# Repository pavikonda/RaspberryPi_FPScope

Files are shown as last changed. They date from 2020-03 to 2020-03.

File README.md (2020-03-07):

# RaspberryPi_FPScope
Fourier ptychographic microscope based on a Raspberry Pi. 

Published as:
Aidukas, T., Eckert, R., Harvey, A.R. et al. Low-cost, sub-micron resolution, wide-field computational microscopy using opensource hardware. Sci Rep 9, 7457 (2019). https://doi.org/10.1038/s41598-019-43845-9

This repository contains an instruction set to build the microscope, CAD files, data acqusition and data processing codes.

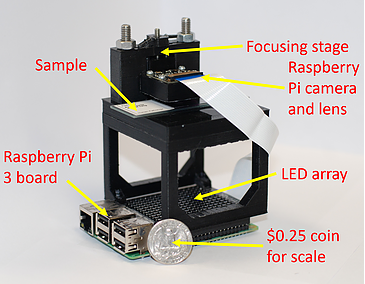
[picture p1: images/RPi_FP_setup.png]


DATA_CAPTURE.py:
This file contains a Python script required to obtain images for Fourier ptychography using a Raspberry Pi computer, Raspberry Pi camera and Unicorn HD LED array. These images are obtained by flashing LEDs in a spiral pattern from the center towards the edges.

CAD Files:
This folder contains .scad and .stl formats of all the parts required to 3D print the microscope. Instructions are outlined in the Supplementary material S1 of our paper.

Fourier ptychographic reconstruction code and test data to use with the reconstruction code can be found at: http://dx.doi.org/10.5525/gla.researchdata.594

Download a Raspbian OS SD card image which includes the necessary libraries from:
https://drive.google.com/open?id=1Z59lnhNKuGGGVIF1KtoCw2bAcdZESKBo

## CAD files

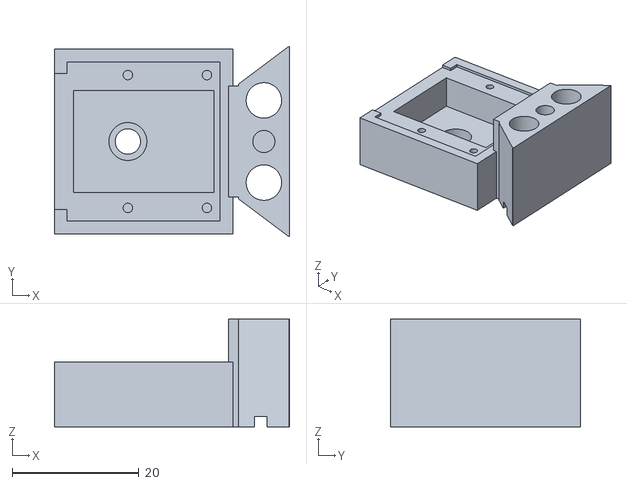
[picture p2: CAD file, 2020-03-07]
CAD files/camera_mount.stl
37.1 x 30.1 x 17.0

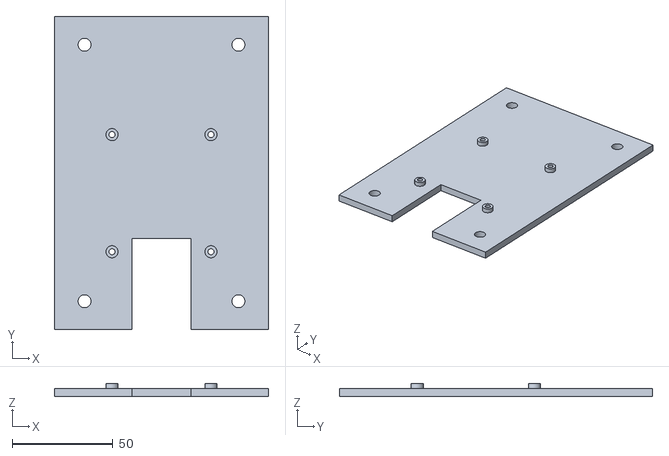
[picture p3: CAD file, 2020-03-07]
CAD files/base.stl
106.0 x 155.0 x 6.50

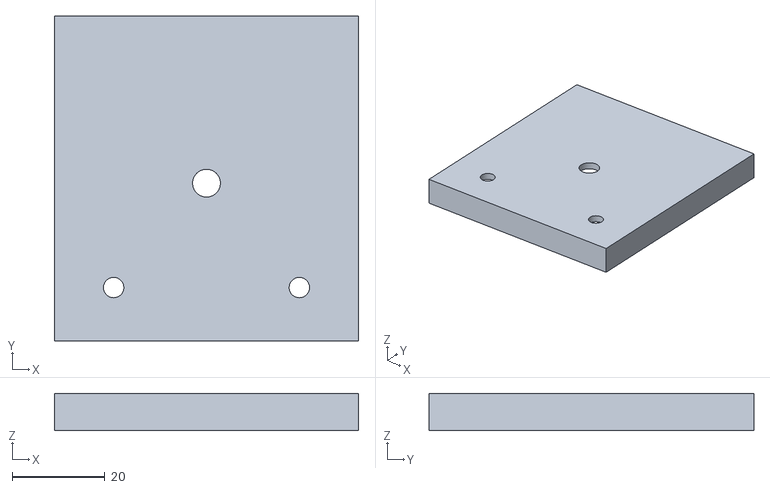
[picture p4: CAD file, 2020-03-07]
CAD files/top.stl
65.5 x 70.0 x 8.00

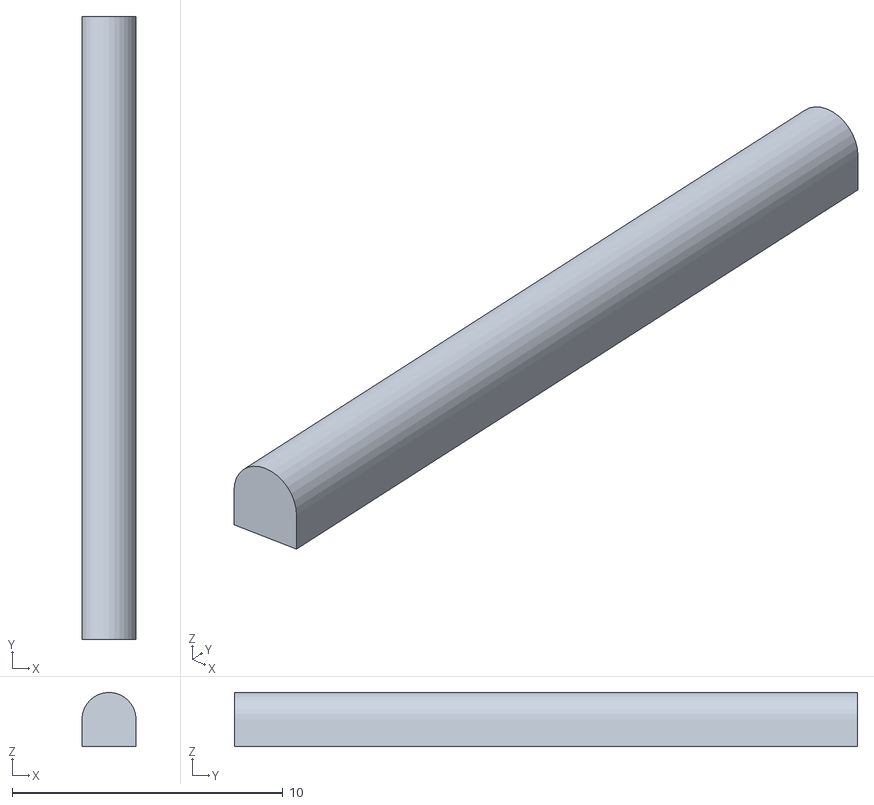
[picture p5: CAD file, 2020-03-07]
CAD files/bar.stl
2.00 x 23.0 x 2.00

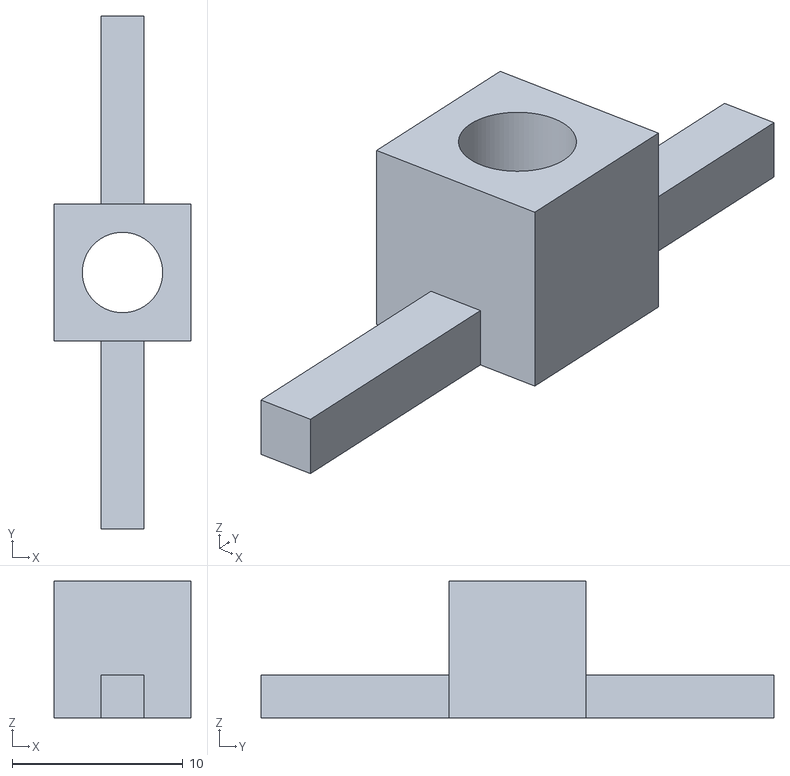
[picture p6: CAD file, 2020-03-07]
CAD files/spring_holder.stl
8.00 x 30.0 x 8.00

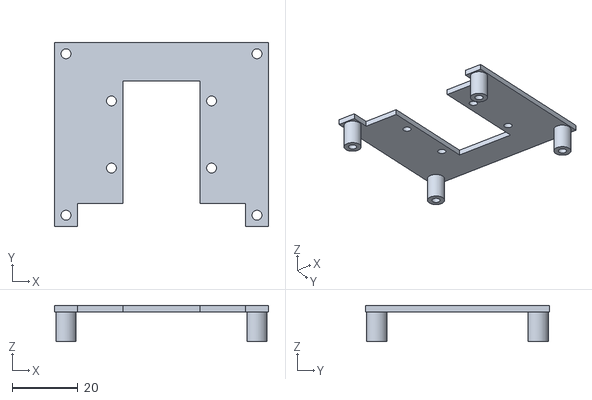
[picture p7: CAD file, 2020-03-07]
CAD files/led_support.stl
65.0 x 56.0 x 11.0

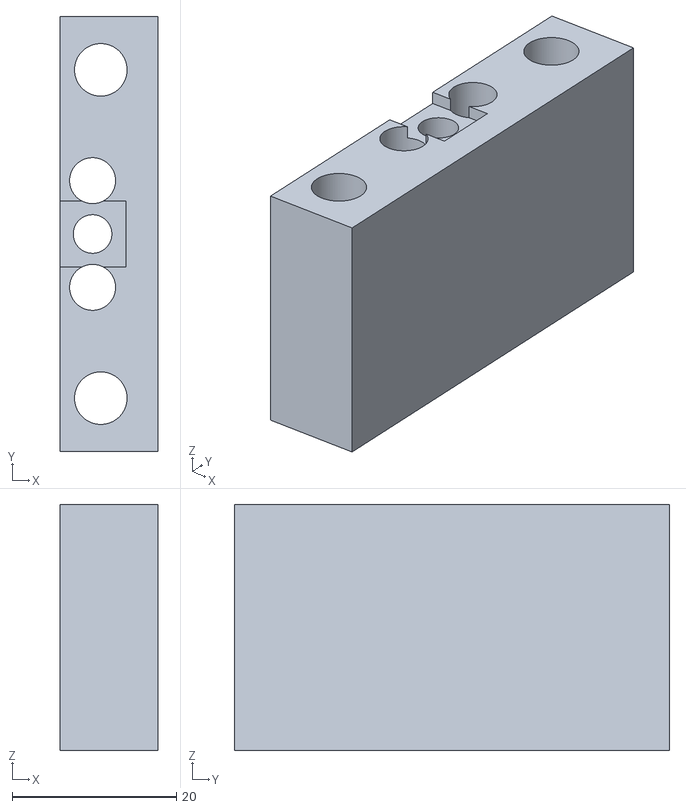
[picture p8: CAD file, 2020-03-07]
CAD files/mount_holder.stl
12.0 x 53.0 x 30.0

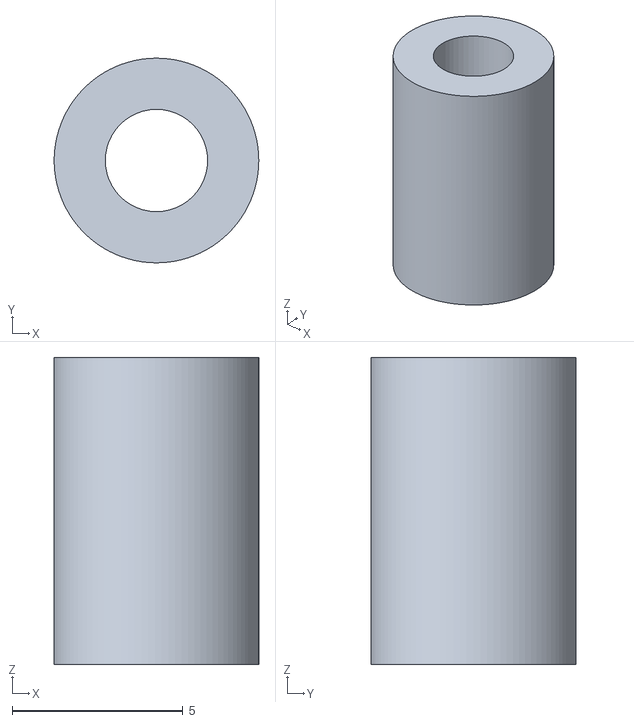
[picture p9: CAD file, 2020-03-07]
CAD files/spacer.stl
6.00 x 6.00 x 9.00

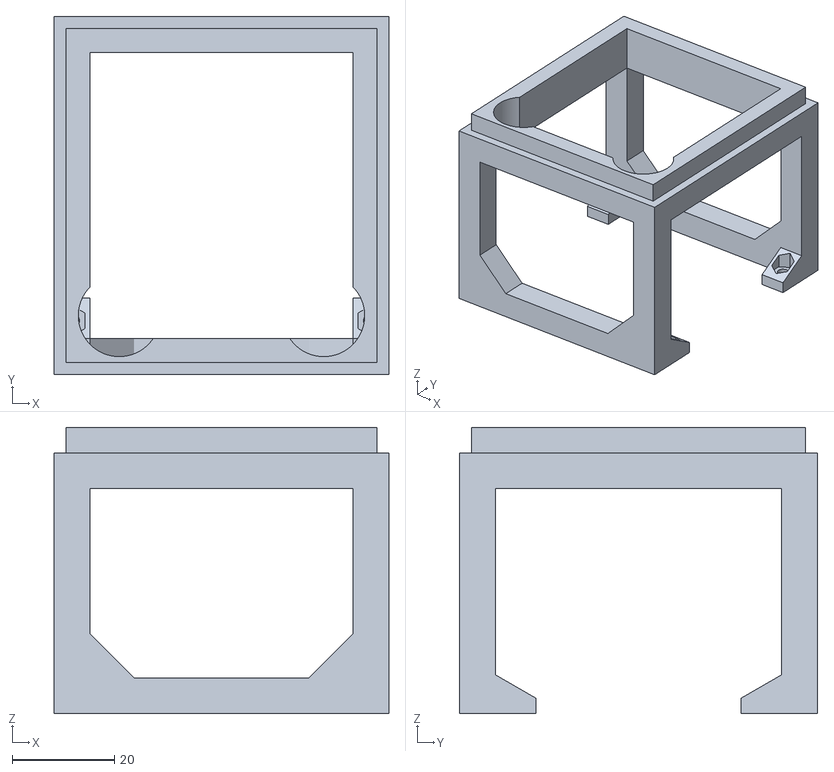
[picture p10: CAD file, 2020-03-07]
CAD files/structure.stl
65.5 x 70.0 x 56.0

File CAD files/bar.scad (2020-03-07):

/*

This is the plastic bar that holds the springs at the bottom of the camera mount (camera_mount.scad)

*/

$fa = 0.2;
$fs = 0.2;

rotate([90,0,0]) cylinder(h=23, r=1,center=true);
translate([0,0,-0.5]) cube([2,23,1], center=true);

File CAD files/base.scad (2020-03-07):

/*

A base for the Raspberry Pi, with attachment holes to mount on an optical table

*/

$fs = 0.2;
$fa = 0.2;

//dimensions of the raspberry pi
pi_width = 56;
pi_length = 85;

//how much the base protrudes from the raspberry pi body
extra_width = 25;
extra_length = 35;

//actual dimensions of the base
total_width = pi_width + extra_width*2;
total_length = pi_length + extra_length*2;
thickness = 4;

//screw dimensions
inner_r = 1.5;
outer_r = 3;
cone_r = 5;

hole_separation_length = 58;
hole_separation_width = 56-3-3-0.5-0.5;

//location of the four holes
hole_x = extra_width + 3 + 0.5;
hole_y = extra_length + 3 + 0.5;
feet_height = 2.5;
hole_height = thickness+feet_height+2;

//location of the four attachment holes
separation = 25.4;
attachment_x = total_width/2 - (separation/2 +separation*1);
attachment_y = total_length/2 - (separation/2 + separation*2);

module foot(){
    cylinder(r=outer_r,h=feet_height);
}
module screw_hole(){
    cylinder(r=inner_r,h=hole_height);
}
module cone_hole(){
    cylinder(r1=cone_r, r2=inner_r,h=thickness);
}
module attachment_hole(){
    cylinder(r=3.2,h=thickness+2);
}

//cutout dimensions
margin = 10;
cutout_x = hole_separation_width-cone_r*2-margin;
cutout_y = extra_length+margin;
module sd_cutout(){
    translate([total_width/2,cutout_y/2-0.01,thickness/2-1]) cube([cutout_x,cutout_y,thickness+3],center=true);
}

module move_raspi_bolts(){
    translate([hole_x,hole_y,0]) children();
    translate([hole_x,hole_y+hole_separation_length,0]) children();
    translate([hole_x+hole_separation_width,hole_y+hole_separation_length,0]) children();
    translate([hole_x+hole_separation_width,hole_y,0]) children();
}

module move_attachment_bolts(){
    translate([attachment_x, attachment_y,-1]) children();
    translate([total_width-attachment_x, attachment_y,-1]) children();
    translate([attachment_x, total_length-attachment_y,-1]) children();
    translate([total_width-attachment_x, total_length-attachment_y,-1]) children();
}

difference(){
    //base with legs
    union(){
        cube([total_width,total_length,thickness]);
        translate([0,0,thickness]) move_raspi_bolts() foot();
    }
    
    //subtract holes from screws
    translate([0,0,-0.001]) move_raspi_bolts(){
        screw_hole(); 
        cone_hole();
    }
    
    //subtract holes for attachment (to the optical table) bolts
    move_attachment_bolts(){
        attachment_hole();
    }
    
    sd_cutout();
}

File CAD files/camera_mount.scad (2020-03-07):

/*

Designed to hold a Raspberry Pi camera module, and fit into mount_holder.scad

Design by Tomas Aidukas, modified by Victor Lovic

*/

// Y is along the cable
camera_w_y = 25.2;
camera_w_x = 24.2;
$fn = 100;
height=14.5-2.8;
wall_thick=4;
lens_height=4;

//Lens is pushed by 1mm from the bottom + its height is 4z.5mm + 6mm distance to the detector lens + the lens sits 6.5mm away from the support. Hence the support should be built 18mm from the bottom
cam_holder = 18;

// Camera platform
difference(){        
        cube([camera_w_x+wall_thick,camera_w_y+wall_thick,height],center=true);
        
    // Crop the top
    translate([0,0,height/2]){
        cube([camera_w_x+1+wall_thick,camera_w_y+1+wall_thick,3],center=true);}
    translate([-10,0,height/2]){
        cube([camera_w_x+10+wall_thick,21.5,4],center=true);}
        
    // Hole inside
    translate([0,0,lens_height]){    
        cube([camera_w_x-2,camera_w_y-9,height+1],center=true);}
    
    // Lens is pushed up by 1mm from the bottomm + its height of 3mm gives 4mm from the bottom of the holder to the top aperture plastic
    translate([-2.5,0,-height/2+lens_height/2+1]){        
        cylinder(d=6, h=lens_height,center=true);}
    
    translate([-2.5,0,-height/2+lens_height/2-1]){        
        cylinder(d=4, h=lens_height,center=true);}
    
    // Camera Holder. The sensor chip sits heigth - 4mm (lens top) - 2mm crop from the top of the lens  = 8mm  . But we also crop 1mm from the bottom of the sensor giving uz 7mm separation from the top lens plastic  to the sensor. Since we need 7.5mm the esensor height = 7.5mm + 2mm + 4mm = 13.5mm
        
    translate([0,0,height/2]){        
        cube([camera_w_x,camera_w_y,4],center=true);}
        
               
    // Camera screw holes
     translate([-24/2+9.5,21/2,height/2-2]){
         cylinder(d=1.5,h=10,center=true);}     
     translate([-24/2+9.5,-21/2,height/2-2]){
         cylinder(d=1.5,h=10,center=true);}
      translate([-24/2+22,21/2,height/2-2]){
         cylinder(d=1.5,h=10,center=true);}
      translate([-24/2+22,-21/2,height/2-2]){
         cylinder(d=1.5,h=10,center=true);}// Camera screw holes END   
         
}



// Slider
// angle is tan(delta_h/slider_hole_w_h)
slider_hole_w_h = 30; 
slider_x_shift_h = 10;
slider_z_shift_h = -10;
delta_h = -20;
$fn = 100;
height1 = height-1.5+2.8+4;
// To get the same angle we need arctan(tan(delta_h/slider_hole_w_h))*slider_hole_w = delta

//30mm is too loose
slider_hole_w = 30; 
slider_x_shift = 10;
slider_z_shift = -10;
//delta = -20;
delta = atan(tan(delta_h/slider_hole_w_h))*slider_hole_w;

camera_w = 25+4;

translate([13,0,height/2+2+2.8+2]){
difference(){
    hull(){
        translate([slider_x_shift,slider_hole_w/2,slider_z_shift]){
            cube([0.1,0.1,height1], center=true);
        }
        
        translate([slider_x_shift,-slider_hole_w/2,slider_z_shift]){
            cube([0.1,0.1,height1], center=true);
        }
        
        translate([slider_x_shift+delta,0,slider_z_shift]){
            cube([0.1,0.1,height1], center=true);
        }
    }    
        // Large block chop
        translate([-18,0,-10]){
            cube([40,70,80], center=true);
        }
            
        //Screw
        translate([6,0,5]){
            cylinder(d=3.5,h=30,center=true);}
        //Screw END 
  
    // Spring Holes
    translate([6,6.5,14.5]){
        cylinder(d=5.6,h=200,center=true);}
    translate([6,-6.5,14.5]){
        cylinder(d=5.6,h=200,center=true);}// Spring Holes END
        
        //spring  holder hole
        translate([5.5,0,-height1-2]){
        cube([2,26,4.2],center=true);}
        
}
    // Connector
    translate([1.8,0,-10]){        
        cube([2.8,camera_w/2+5-2,height1],center=true);}
   
   /*     
// Spring holder
    translate([5.5,3,-height1-3.5]){
        cube([1,7,2]);}
        
    translate([5.5,-10,-height1-3.5]){
        cube([1,7,2]);}// Spring holder END
        
    */
}


    

    
// Connector 2.5mm length
// Centre to connector 29/2 = 14.5mm 
// slider is 6.8mm
// Total: 23.8mm from the centre to the edge
    
// Holder mount to back is 10.3mm
// 2.2 and 1.6 are the edge thicknesses around the screw. 6.4mm is the screw thickness. So, 1.6mm + 3.2mm = 4.8mm from the wall to the center.
    
// Final Calc gives 4.8mm + 23.8mm = 28.6mm from the centre to where the holes should be

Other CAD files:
CAD files/led_support.scad
CAD files/mount_holder.scad
CAD files/prism.scad
CAD files/spacer.scad
CAD files/spring_holder.scad
CAD files/structure.scad
CAD files/top.scad
CAD files/wedge.scad

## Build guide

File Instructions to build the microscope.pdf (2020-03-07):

1 | Low-cost, sub-micron resolution, wide-
2 | field computational microscopy using
3 | opensource hardware

4

TOMAS AIDUKAS¹, REGINA ECKERT², ANDREW R. HARVEY¹* 5 | ,
LAURA WALLER², PAVAN C. KONDA¹ 6
1 7 | Imaging Concepts Group, School of Physics and Astronomy, University of Glasgow, Scotland, G12 8QQ, UK
8 | 2Department of Electrical Engineering and Computer Sciences, University of California, Berkeley, California
9 | 94720, USA
10 | *Andy.Harvey@glasgow.ac.uk

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
# Supplementary material 1: Instructions to build a Raspberry Pi Fourier ptychographic computational microscope

This document provides instructions to build a low-cost computational microscope reported in the manuscript: “Low-cost, sub-micron resolution, wide-field computational

## microscopy using opensource hardware”. The CAD files and data acquisition codes

36 | can be downloaded from | http://dx.doi.org/10.5525/gla.researchdata.594.

### Introduction

One of the aims when building this microscope was to use only off-the-shelf components that can be easily bought anywhere and to design the microscope in such a way that it could be assembled with minimal external components. Avoiding complexity allowed us to build a very low-cost and robust microscope, which can be assembled and used with opensource software. Designs for the parts were made using OpenSCAD open source CAD software and printed with Ultimaker 2+ 3D printer.

The microscope was designed around the Raspberry Pi 3 computer board due to a wide opensource community and the support available. The computer itself has a CSI port to which a Raspberry Pi camera can be connected. For the illumination we used a Unicorn HAT HD 16x16 LED array, which is an add-on designed for the Raspberry Pi boards. It mounts directly onto the GPIO pins on top of the board. Camera and the LED board can be connected and controlled easily via opensource libraries available for Python or C++ programming languages.

Furthermore, Raspberry Pi camera comes mounted with a mobile-phone-camera type lens. It was unscrewed from the camera and used as our microscope objective. The component list required to build the setup is provided below, along with a stepby-step instruction set for assembly and operation of the microscope.

56 | Component list
Off-the-shelf components | Quantity | Purpose | Suppliers and manufacturers
Raspberry Pi 3 computer board (~$32) | 1 | Controlling the camera and LED array; image capture and storage | Multiple suppliers (e.g. Pimoroni, Farnell, RS)
20mm long M3 screws (unit price of ~$0.05) | 4 | Fix Raspberry Pi computer board to a stable base | Multiple suppliers (e.g. RS)
Unicorn HAT HD 16x16 LED array (~$30) | 1 | Illumination source | Pimoroni
Raspberry Pi V2.1 NoIR camera (~$20) | 1 | Image sensor | Multiple suppliers (e.g. Pimoroni, PiHut)
Unscrewed lens from the Raspberry Pi camera (Part 4) | 1 | Microscope objective
3.5mm diameter, >10mm long, 0.25mm pitch screw and bushing (Thorlabs F3ES25, F3ESN1P) (~$7, could use a regular screw to reduce cost) | 1 | Used for high-accuracy focusing | Thorlabs
>40mm long M6 screws + nuts (unit price of ~$0.05) | 2 | Attaching the focusing stage to the sample stage | Multiple suppliers (e.g. RS)
5.6mm diameter, ~10mm long springs (RS Stock No. 821-431) (~$1, or any other stiff spring) | 2 | Counter balance force for the focusing stage | Multiple suppliers (e.g. RS)
5mm long M1.5 screws (unit price of ~$0.05) | 4 | Screwing Raspberry Pi (part 4) camera to the focusing stage | Multiple suppliers (e.g. RS)
57 | Supplementary Table S1 1. List of the off-the-shelf components required to build the
58 | microscope. Several links for the products are provided at the end of the document.

59

60

61

### Design

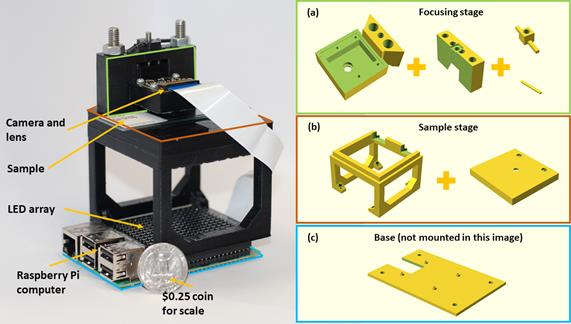
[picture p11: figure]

Supplementary Figure S1 1. The experimental setup with all the necessary annotations for reference to 3D printed designs.

Supplementary Figure S1 1 shows the assembled setup together with 3D printed parts required. It was built using components described in Supplementary Table S1 1. Once each component is 3D printed, the assembly is very simple and requires only a few screwdrivers.

Base

The plastic base shown in Supplementary Figure S1 1(c) was printed such that the Raspberry pi and the sample stage could be screwed onto it. The base itself has 4 holes which can be used for screwing the microscopes to the optical bench if needed. This was designed to provide higher stability when longitudinal imaging might be required.

Sample stage

The sample stage shown in Supplementary Figure S1 1(b) was designed to be mounted on the Raspberry Pi board with an LED array on top. The four screw holes on the 3D printed sample stage match those found on the Raspberry Pi and the plastic base. All components can be screwed tightly together to form a single microscope unit.

There is another 3D printed part that goes on top of the sample stage legs. It has 3 holes on it where the central one acts as an aperture for the sample, reducing any stray light and reflections from the LED array. The other 2 holes were made for screws that attach the focusing stage to the sample stage.

Camera holder and focusing stage

The focusing stage shown in Supplementary Figure S1 1(a) is composed of four 3D printed elements.

The camera holder module (the first 3D printed part seen in Supplementary Figure S1 1(a)) was designed to mount the microscope objective (the unscrewed camera lens) in place and screw the camera above it. This was designed for finite-conjugate microscope configuration to be established. The unscrewed lens from the camera has a 1.5mm aperture only on one side; lens must be mounted such that the aperture is facing downwards (towards the sample). This compact design was set to achieve 1.5× magnification, but it can be easily modified by changing the distance between the lens and the detector. It should be noted that the sensor is not glued to the camera board well. To ensure correct alignment it is best to re-glue the sensor.

The camera holder mount, (the second 3D printed part seen in Supplementary Figure S1 1(a)) serves several purposes including focusing the sample. Firstly, it has rails onto which camera holder module is mounted and can be moved up or down for focusing. The central hole in the camera holder mount is for the 0.25mm pitch screw. Springs are fed through the inner pair of holes in the camera holder mount and the corresponding holes in the camera holder module. They are held in place by sliding the pins shown in Supplementary Figure S1 1(a) through each end of both springs. The screw is used to push down on the camera holder module while the springs and bottom pin provide a counter force to push it upwards. This way the module can slide along the rails with high-precision, by turning the screw. Springs provide stability and push the module upwards when the screw does not provide a downward force anymore, which should minimize the backslash error.

Secondly, the outer holes in the camera holder mount enables addition of screws or bolts to attach the whole focusing module to the top of the sample stage. While the focusing is done via a translation stage, the sample must be translated by hand. In our setup, the FOV is large so precise translation is not required; hence, we chose to use this design. However, there are 3D printed sample translation stages available in the opensource community that can be integrated into our design.

### Assembly instructions

Access to a 3D printer is required to print several parts required for the assembly. We used Ultimaker 2+ with a nozzle size of 0.25mm for the camera holder module and 0.4mm for the other components. Also, the lens from the Raspberry Pi V2.0 camera must be unscrewed before the assembly. Step-by-step instructions to assemble the microscope:
1. 3D print all the parts using a printer of your choice. We used openSCAD to design, render and save the designs in .STL format. CURA software was used to create the files that can be read by the Ultimaker 2+ 3D printer. Black PLA filament and a 0.4mm diameter nozzle was used for printing the sample stage parts, while a 0.25mm nozzle was used to print the focusing stage. Our files were designed to match the tolerance of the nozzles on our printer. The 3D models need to be tweaked when a different nozzle size or a different 3D printer is used due to change in the tolerances.
2. Connect the Raspberry Pi camera to the Raspberry Pi board.

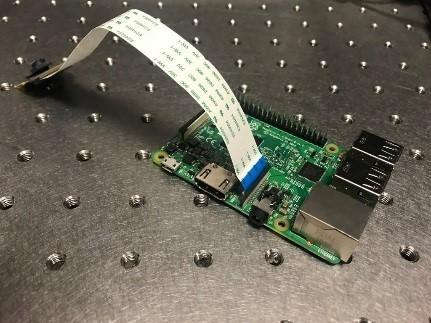
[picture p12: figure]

3. Mount the LED array on top of the Raspberry Pi board by plugging it into the GPIO pins on the board.

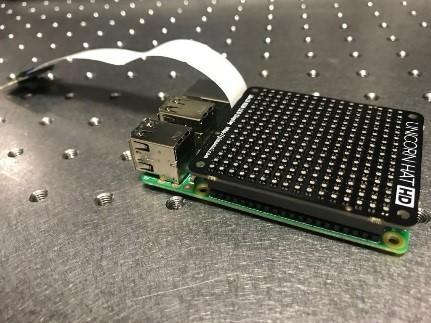
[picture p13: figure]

4. Place the sample stage such that the screw holes match the base; making sure that the sample-stage feet are not on top of any of the LEDs. Then place a nut in each foot of the sample stage.
5. Place the spacers in between the Raspberry Pi board UnicornhatHD board so that they are aligned with the screw holes and then screw the Raspberry Pi board and the sample stage to the base such that they form a single rigid module.

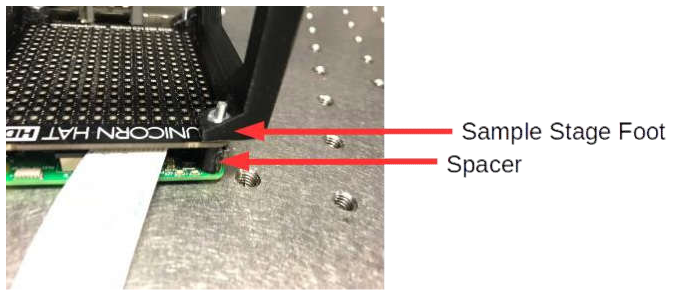
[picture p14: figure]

6. Take the camera holder; place the lens in the circular slot with the aperture facing downwards, towards the sample stage.

144

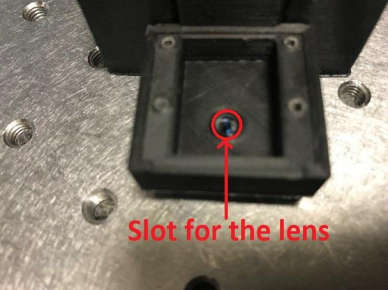
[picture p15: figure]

145 | 7. Mount the camera, align with the screw holes of the 3D printed camera holder;
146 | screw it in place tightly.

147

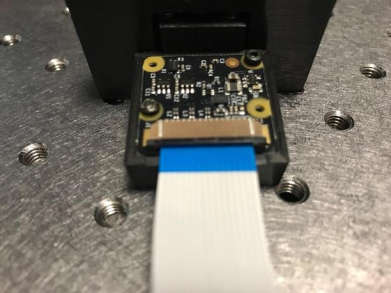
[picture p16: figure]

148 | 8. Slide the camera holder module onto the focusing stage rails. Thread the
149 | springs through the holes on the focusing stage and the camera module as
150 | shown by a red arrow in the figure below. Use two 3D printed horizontal pins
151 | seen in Supplementary Figure S1 1(a)) to hold the ends of the springs at the
152 | top and bottom of the focusing stage; the spring should be long enough such
153 | that it is stretched out and apply a strong counter-balance force to the screw.

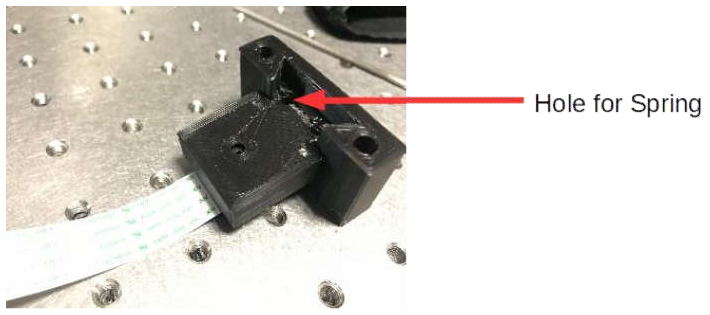
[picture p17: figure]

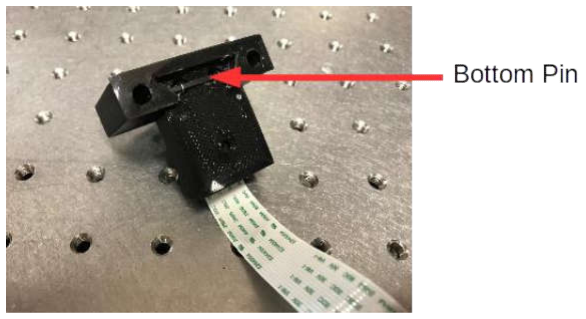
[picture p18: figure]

9. Pull down the camera holder module and, from underneath, place the bushing up into the central hole of the focusing stage. Then, place the screw in the top of the camera holder mount. Screw it in such that the screw pushes onto the camera holder module.

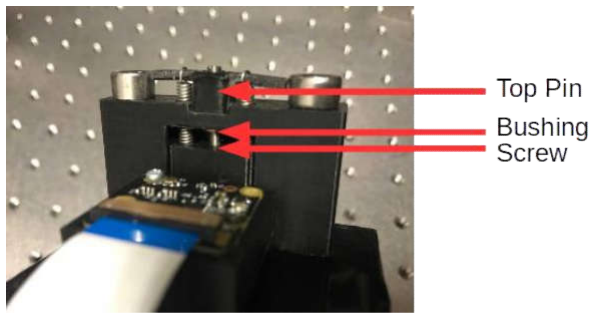
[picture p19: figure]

10. Use screws with nuts to fix the focusing stage tightly to the top plate of the sample stage from Supplementary Figure S1 1(b)).
11. Place the focusing stage module onto the sample stage module with the Raspberry Pi computer. The part is designed to have a tight fit, if it is not tight, please adjust the tolerances.
12. Optional: connect a screen using the HDMI port.
13. Optional: connect a keyboard and a mouse.
14. Optional: Place the Raspberry Pi board on top of the 3D printed base; align the base and the Raspberry Pi such that the screw holes are on top of each other.

171

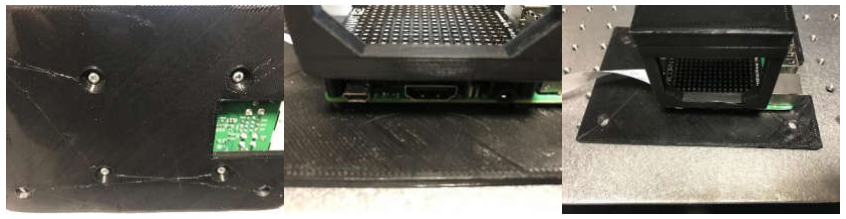
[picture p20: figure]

172 | Operating the Microscope
173 | Installing Software on the Raspberry Pi
174 | Raspbian is a free Raspberry Pi operating system available for download from the
175 | manufacturer's website. It can be installed by following the guide listed in the Links
176 | section.
177 | The various interfaces of the Raspberry Pi can be enabled by going to
178 | Applications Menu -> Preferences -> Raspberry Pi Configuration -> Interfaces, and
179 | then enabling all options.
180 | Image acquisition codes can also be downloaded from the Links section. Various
181 | python packages will need to be installed before these can be used. The packages
182 | needed are:
183 | • Unicornhathd
184 | • Numpy
185 | • Picamera
186 | • Matplotlib
187 | • Io
188 | • Random
189 | • Fractions
190 | These can be installed using the pip package management system or by installing
191 | anaconda on the raspberry pi. However, the picamera and unicornhathd packages are
192 | not included in anaconda and will need to be installed separately. Links to the
193 | installation guides of these packages and a more general guide to installing python
194 | packages on the Raspberry Pi are provided in the Links section. Python2 is used for
195 | image acquisition so follow instructions for Python2.7 as opposed to Python3.
196 | We have also provided a cloned Raspberry Pi image which can be cloned onto
197 | an SD card:
198 | https://drive.google.com/open?id=1Z59lnhNKuGGGVIF1KtoCw2bAcdZESKBo. You
199 | can download it and clone onto an SD card by following this tutorial
200 | https://beebom.com/how-clone-raspberry-pi-sd-card-windows-linux-macos/. The
201 | cloned image contains image capture codes and all the required packages pre-
202 | installed for easy plug-and-play operation of the microscope.
203 | Data Acquisition
204 | 1. Connect the Raspberry Pi to a keyboard, mouse and monitor, and turn it on.
205 | 2. Place the sample on the top plate of the sample stage, underneath the
206 | camera mount.

207 | 3. Use the "Focusing" script to make sure the sample is positioned correctly and
208 | in focus. This script has an option to zoom that can be used if needed. To
209 | focus the microscope, use an Allen key to turn the screw in the focusing
210 | stage.
211 | 4. Close the preview and open the "main data acquisition" file.
212 | 5. Adjust the necessary parameters in the data acquisition file and save the file.
213 | 6. Place the microscope in a dark room or cover it, being careful to ensure the
214 | sample is not moved and the focus is not shifted.
215 | 7. Run the data acquisition script.
216 | 8. Switch off the Raspberry Pi after data acquisition is complete.
217 | Data transfer
218 | The captured data can be copied by a USB drive or the SD card on the Pi can
219 | be inserted into a PC and disk internals Linux reader can be used to copy the data.
220 | Data can also be transferred through the internet or an Ethernet cable. One possible
221 | approach is by transferring files using a file transfer protocol (FTP)
222 | https://www.dexterindustries.com/howto/how-to-transfer-files-to-your-raspberry-pi-
223 | from-a-pc-computer/. Another approach is to transfer files to a cloud storage location
224 | (e.g. OneDrive or Dropbox) and retrieve the files with another computer.

225

226 | Links
227 | • Data acquisition codes and CAD files:
228 | http://dx.doi.org/10.5525/gla.researchdata.594
229 | • Raspbian installation guide:
230 | https://www.raspberrypi.org/documentation/installation/installing-
231 | images/README.md
232 | • Needs Etcher software to install Raspbian on the SD Card
233 | • But first, download the Raspbian image from the above link.
234 | • Guide to Installing Python Packages on Raspberry Pi:
235 | https://www.raspberrypi.org/documentation/linux/software/python.md
236 | • Picamera installation guide: https://picamera.readthedocs.io/en/release-1.13/
237 | • UnicornHatHD installation guide: https://www.github.com/pimoroni/unicorn-
238 | hat-hd
239 | • Pimoroni Unicorn HD LED array: https://shop.pimoroni.com/products/unicorn-
240 | hat-hd
241 | • Raspberry Pi V2.1 camera: https://www.raspberrypi.org/products/camera-
242 | module-v2/
243 | • DiskInternals Linux Reader can be used to read the files on a Linux SD card
244 | from a computer: https://www.diskinternals.com/linux-reader/
245 | • Installing a cloned Raspberry Pi image to an SD card:
246 | https://beebom.com/how-clone-raspberry-pi-sd-card-windows-linux-macos/
247 | • Raspberry Pi cloned image used for this microscope:
248 | https://drive.google.com/open?id=1Z59lnhNKuGGGVIF1KtoCw2bAcdZESKB
249 | o
